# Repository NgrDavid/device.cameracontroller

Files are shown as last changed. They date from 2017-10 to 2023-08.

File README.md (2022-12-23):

## Harp Camera Trigger Control

This device allows to trigger up to 2 cameras at a predefined frequency pulse or 2 servo motors. Connect cameras to CAM0 TRIG and CAM1 TRIG ports.

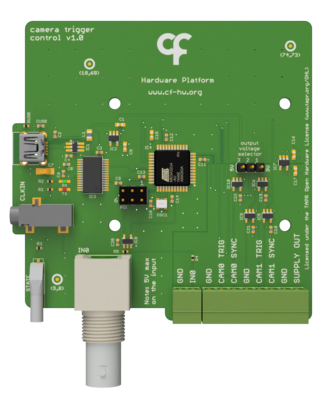
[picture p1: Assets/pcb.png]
harpcameratriggercontrol


### Key Features ###

* Separate sample frequency for each camera
* Alternate between camera triggering and servo motor control
* Each camera output can be handled as pure digital output

### Connectivity ###

* 1x clock sync input (CLKIN) [stereo jack]
* 1x USB (for computer) [USB type B]
* 1x 5V supply out [screw terminal]
* 4x digital outputs (I/O interface for 2 cameras): CAM0 TRIG, CAM0 SYNC, CAM1 TRIG, CAM1 SYNC [screw terminal]
* 1x digital input for general purpose or camera control (IN0) [BNC]

## Interface ##

The interface with the Harp board can be done through [Bonsai](https://bonsai-rx.org/) or a dedicated GUI (Graphical User Interface).

In order to use this GUI, there are some software that needs to be installed:

1 - Install the [drivers](https://bitbucket.org/fchampalimaud/downloads/downloads/UsbDriver-2.12.26.zip).

2 - Install the [runtime](https://bitbucket.org/fchampalimaud/downloads/downloads/Runtime-1.0.zip).

3 - Reboot the computer.

4 - Install the [GUI](https://bitbucket.org/fchampalimaud/downloads/downloads/Harp%20Camera%20Controller%20v1.0.1.zip).

## Licensing ##

Each subdirectory will contain a license or, possibly, a set of licenses if it involves both hardware and software.

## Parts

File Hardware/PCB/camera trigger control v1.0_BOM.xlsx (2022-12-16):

Part(s) | Quantity | Description | Distributor | Part. No.
IC1 | 1 | ESD Protection Low Cap | Mouser | 511-USBLC6-2SC6
IC2, IC7 | 2 | LDO 250mA Ultra-Lo Noise LDO Reg | Mouser | 595-LP5907MFX-3.3NPB
IC3 | 1 | IC USB USB to Serial UART Enhanced IC SSOP-28 | Mouser | 895-FT232RL
IC4 | 1 | ATXMEGA64A4U-AU, ATxmega, 32 MHz, 64 KB, 4 KB, 44, TQFP | Mouser | 556-ATXMEGA64A4U-AU
IC5, IC6, IC9, IC10 | 4 | Buffers e line drivers 1.65-5.5V Single Non-Inverting TTL | Mouser | 863-M74VHC1GT50DTT1G
IC8 | 1 | SingleBuffer / Driver, 1.65V to 5.5V, SOT-23-5 | Mouser | 595-SN74LVC1G125DBVR
C3, C4 | 2 | CAP CER 47pF 50V ±5% C0G 0402 | Mouser | 77-VJ0402A470JXACBC
CUSB | 1 | CAP CER 4.7nF 100V ±10% X7R 0402 | Mouser | 81-GRM155R72A472KA01
C2, C6, C8, C9, C10, C11, C12, C13, C18, C19, C20, C21, C22 | 13 | CAP CER 100nF 10V X5R 0402 | REEL | REEL
C14 | 1 | CAP CER 0.33uF 10V ±10% X5R 0402 | Mouser | GRM155R61A334KE15D
C7 | 1 | CAP TAN 4.7uF 6.3V ±10% 1206 | Mouser | 80-T491A475K006
C1, C5, C15, C16, C17 | 5 | CAP CER 10uF 10V ±10% X5R 0603 | Mouser | 81-GRM188R61A106KE9D
R1, R2 | 0 | DNI | DNI | DNI
R3 | 1 | RES SMD 68Ω OHM 5% 0402 | Mouser | 71-CRCW0402-68-E3
R4 | 1 | RES SMD 330Ω OHM 1% 0402 | Mouser | 667-ERJ-PA2F3300X
R5 | 1 | RES SMD 100kΩ 1% 0402 | REEL | REEL
RUSB | 1 | RES SMD 1MΩ 1% 0402 | Mouser | 652-CR0402FX-1004GLF
L1 | 1 | 40ohms 100MHz 1.5A Monolithic 0805 SMD | Mouser | 875-MI0805K400R-10
STATE | 1 | LED, Green, 1.6mm x 0.8mm, 566 nm, 2.1 V, 20 mA, 15 mcd | Mouser | 78-TLMP1100-GS08
RX, TX | 0 | DNI | DNI | DNI
OSC1 | 1 | 32MHz 10ppm | Mouser | 998-1001CI5032.0000T
PDI | 1 | 6P DR UNSHRD HRD | Mouser | 649-67996-206HLF
JP1 | 1 | 3POS Gold Male | Mouser | 649-68001-203HLF
 | 1 | SHUNT JUMPER, 2POS | Farnell | 2396301
USB | 1 | UX60-MB-5S8 | Mouser | 798-UX60-MB-5S8
USB Cable | 1 | USB A - MINI-B 0.8M - MINI-B 0.8M BLACK | Mouser | 538-88732-8502
IN0 | 1 | R.A. JACK 50 OHM | Mouser | 571-5227161-1
CLKIN | 1 | SMT 3.5 STEREO REEL | Mouser | 502-35RASMT2BHNTRX
 | 1 | Tubos de Luz LED CML LIGHTPIPE | Mouser | 606-7513D2-L
 | 1 | IMO 20.1550M/8-E Pluggable Terminal Block, 3.5 mm, 8 Ways | Farnell | 2575220
 | 1 | IMO 20.1550M/2-E Pluggable Terminal Block, 3.5 mm, 2 Ways | Farnell | 2575215
X1 | 1 | Horizontal, Header, 3.5 mm, 2 Ways, 10 A, 250 V, Through Hole Right Angle | Farnell | 20.155MH/2-E
X2 | 1 | Horizontal, Header, 3.5 mm, 8 Ways, 10 A, 250 V, Through Hole Right Angle | Farnell | 20.155MH/8-E
Components | 52
Licensed under the TAPR Open Hardware License (www.tapr.org/OHL)
Copyright 2017 Artur Silva and Filipe Carvalho

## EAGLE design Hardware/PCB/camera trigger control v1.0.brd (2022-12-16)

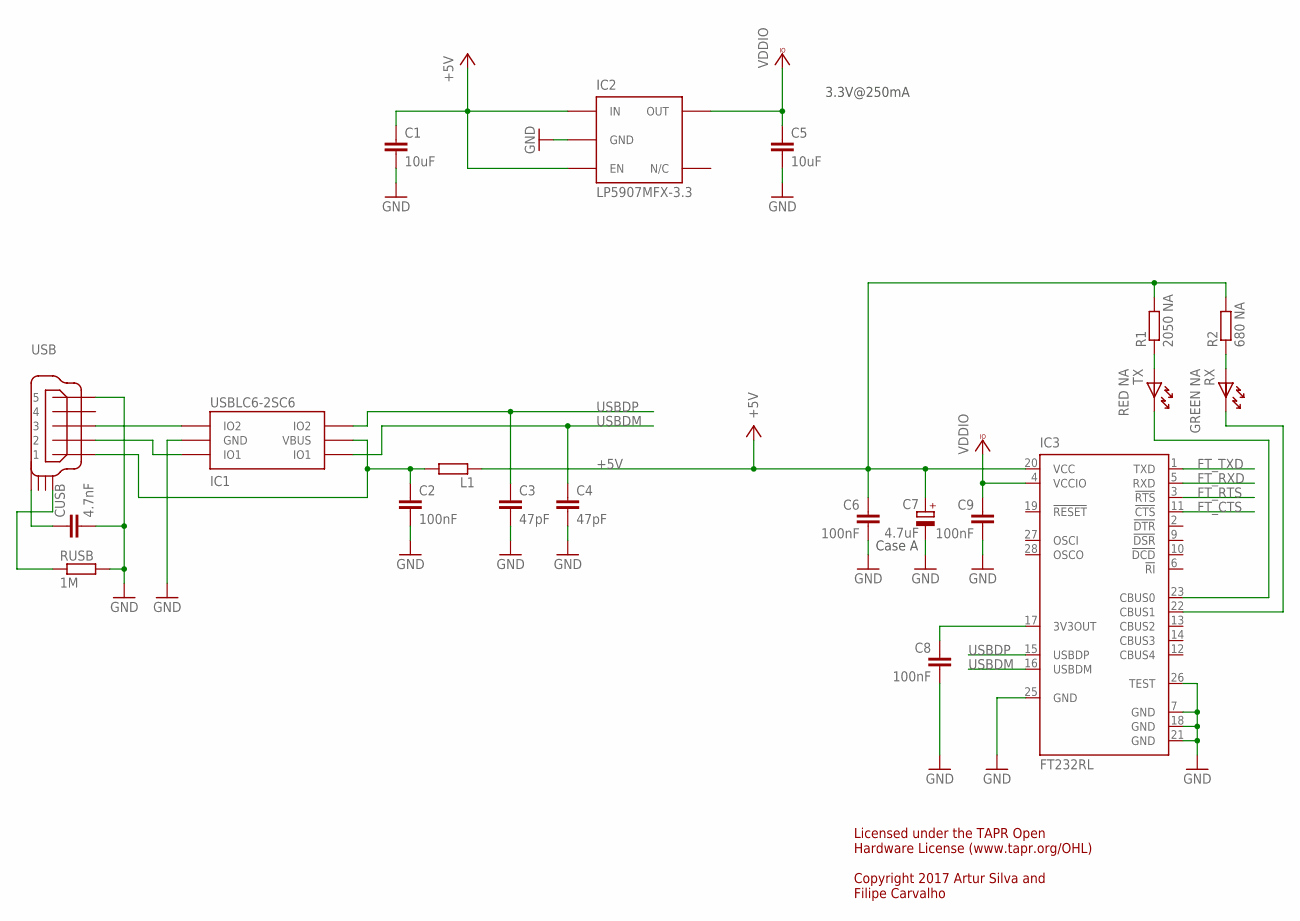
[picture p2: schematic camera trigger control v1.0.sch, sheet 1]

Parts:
C1, C5: 10uF; C0603
C2, C6, C8, C9: 100nF; C0402
C3, C4: 47pF; C0402
C7: 4.7uF; A/3216-18W
CUSB: 4.7nF; C0402
IC1: USBLC6-2SC6; SOT23-6L
IC2: LP5907MFX-3.3; TSOT23-5
IC3: FT232RL; SSOP28
L1: ???; R0805
R1: 2050 NA; R0402
R2: 680 NA; R0402
RUSB: 1M; R0402
RX: GREEN NA; LED_HAND
TX: RED NA; LED_HAND
USB: USB_MINI_B; 240-0002-1

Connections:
+5V: C1.1, C6.1, C7.+, IC2.1 (IN), IC2.3 (EN), IC3.20 (VCC), L1.1, R1.2, R2.2; also elsewhere on the board
FT_CTS: IC3.11 (!CTS); also elsewhere on the board
FT_RTS: IC3.3 (!RTS); also elsewhere on the board
FT_RXD: IC3.5 (RXD); also elsewhere on the board
FT_TXD: IC3.1 (TXD); also elsewhere on the board
GND: C1.2, C2.2, C3.2, C4.2, C5.2, C6.2, C7.-, C8.2, C9.2, CUSB.2, IC1.P$2 (GND), IC2.2 (GND), IC3.7 (GND), IC3.18 (GND), IC3.21 (GND), IC3.25 (GND), IC3.26 (TEST), RUSB.2, USB.P$5 (5); also elsewhere on the board
unnamed: C8.1, IC3.17 (3V3OUT)
unnamed: C2.1, IC1.P$5 (VBUS), L1.2, USB.P$1 (1)
unnamed: IC1.P$1 (IO1), USB.P$2 (2)
unnamed: R2.1, RX.A
unnamed: IC3.23 (CBUS0), TX.K
unnamed: IC3.22 (CBUS1), RX.K
unnamed: IC1.P$3 (IO2), USB.P$3 (3)
unnamed: CUSB.1, USB.SHIELD_4
unnamed: RUSB.1, USB.SHIELD_1
unnamed: R1.1, TX.A
USBDM: C4.1, IC1.P$6 (IO1), IC3.16 (USBDM)
USBDP: C3.1, IC1.P$4 (IO2), IC3.15 (USBDP)
VCCIO: C5.1, C9.1, IC2.5 (OUT), IC3.4 (VCCIO); also elsewhere on the board

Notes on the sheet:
Case A
3.3V@250mA
Licensed under the TAPR Open Hardware License (www.tapr.org/OHL) Copyright 2017 Artur Silva and Filipe Carvalho

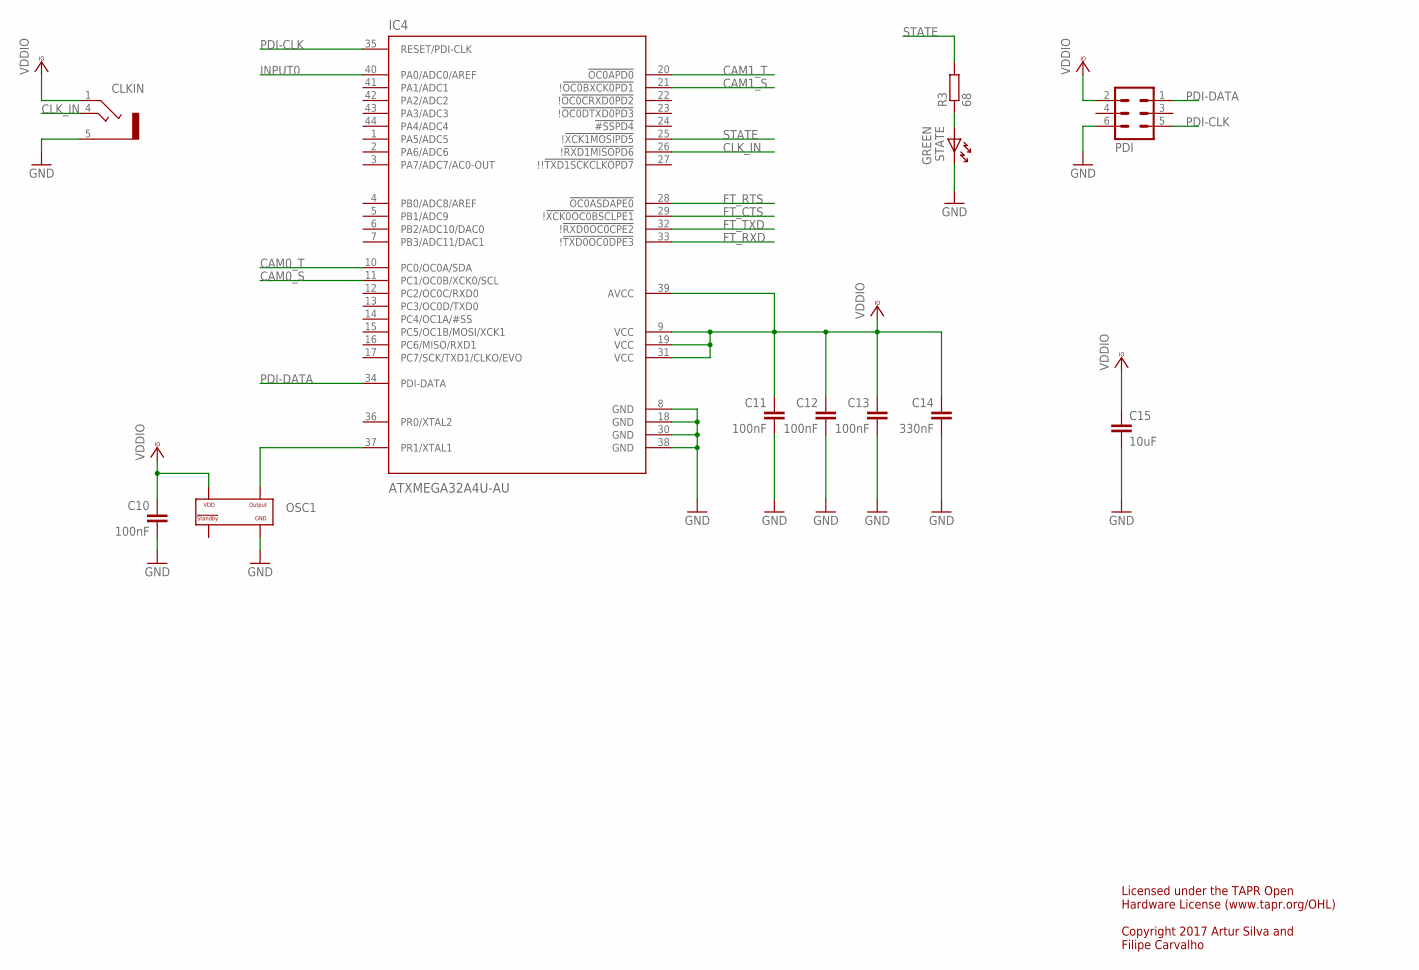
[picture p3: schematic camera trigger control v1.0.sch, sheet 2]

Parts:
C10, C11, C12, C13: 100nF; C0402
C14: 330nF; C0402
C15: 10uF; C0603
CLKIN: STEREO_JACK; 35RASMT2BHNTRX
IC4: ATXMEGA32A4U-AU; QFP80P1200X1200X120-44N
OSC1: OSCILLATOR; OSCILLATOR_3.2X2.5
PDI: MA03-2
R3: 68; R0402
STATE: GREEN; LED_HAND

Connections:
CAM0_S: IC4.11 (PC1/OC0B/XCK0/SCL); also elsewhere on the board
CAM0_T: IC4.10 (PC0/OC0A/SDA); also elsewhere on the board
CAM1_S: IC4.21 (!!OC0BXCK0PD1); also elsewhere on the board
CAM1_T: IC4.20 (!OC0APD0); also elsewhere on the board
CLK_IN: CLKIN.4, IC4.26 (!!RXD1MISOPD6)
FT_CTS: IC4.29 (!!XCK0OC0BSCLPE1); also elsewhere on the board
FT_RTS: IC4.28 (!OC0ASDAPE0); also elsewhere on the board
FT_RXD: IC4.33 (!!TXD0OC0DPE3); also elsewhere on the board
FT_TXD: IC4.32 (!!RXD0OC0CPE2); also elsewhere on the board
GND: C10.2, C11.2, C12.2, C13.2, C14.2, C15.2, CLKIN.5, IC4.8 (GND), IC4.18 (GND), IC4.30 (GND), IC4.38 (GND), OSC1.P$2 (GND), PDI.6, STATE.K; also elsewhere on the board
INPUT0: IC4.40 (PA0/ADC0/AREF); also elsewhere on the board
unnamed: R3.1, STATE.A
OSC1: IC4.37 (PR1/XTAL1), OSC1.P$3 (OUTPUT)
PDI-CLK: IC4.35 (RESET/PDI-CLK), PDI.5
PDI-DATA: IC4.34 (PDI-DATA), PDI.1
STATE: IC4.25 (!!XCK1MOSIPD5), R3.2
VCCIO: C10.1, C11.1, C12.1, C13.1, C14.1, C15.1, CLKIN.1, IC4.9 (VCC), IC4.19 (VCC), IC4.31 (VCC), IC4.39 (AVCC), OSC1.P$4 (VDD), PDI.2; also elsewhere on the board

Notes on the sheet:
Licensed under the TAPR Open Hardware License (www.tapr.org/OHL) Copyright 2017 Artur Silva and Filipe Carvalho

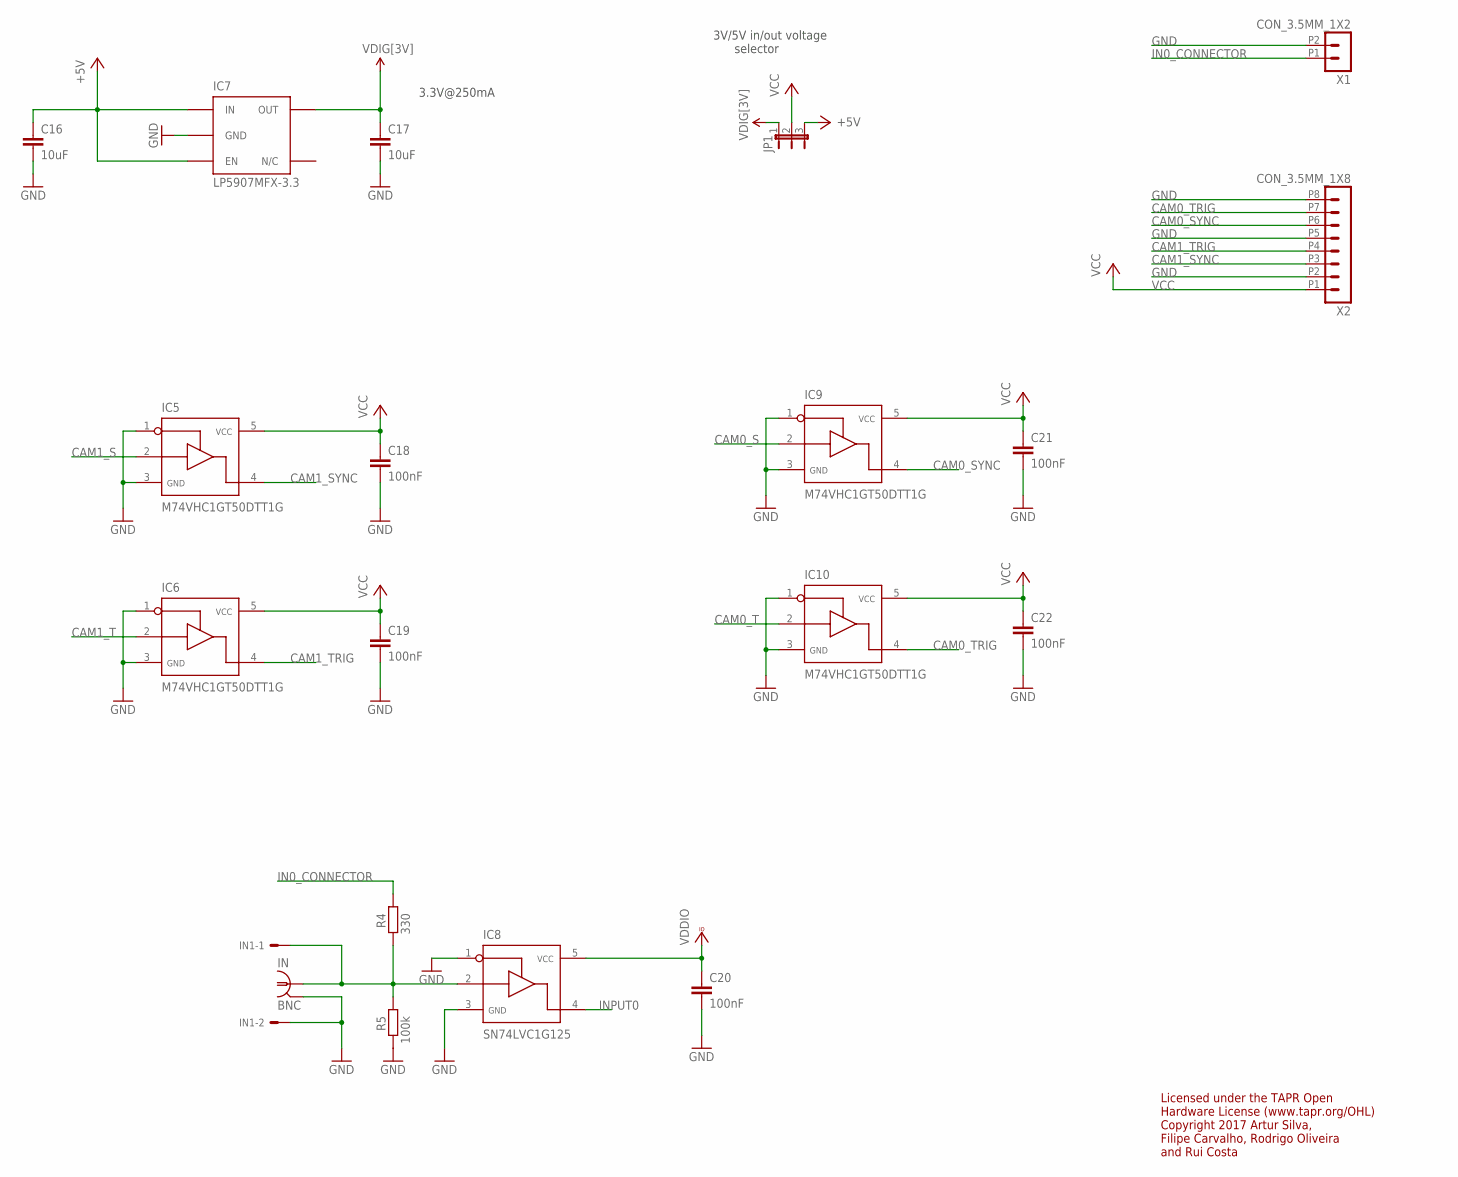
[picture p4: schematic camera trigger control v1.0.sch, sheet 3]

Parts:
C16, C17: 10uF; C0603
C18, C19, C20, C21, C22: 100nF; C0402
IC5, IC6, IC9, IC10: M74VHC1GT50DTT1G; SOT23-5
IC7: LP5907MFX-3.3; TSOT23-5
IC8: SN74LVC1G125; SOT23-5
IN: BNC; BNC_RA
IN1: 22-05-7028-02; 7395-02
JP1: JP2E; JP2
R4: 330; R0402
R5: 100k; R0402
X1: CON_3.5MM_1X2
X2: CON_3.5MM_1X8

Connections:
+5V: C16.1, IC7.1 (IN), IC7.3 (EN), JP1.3; also elsewhere on the board
CAM0_S: IC9.2; also elsewhere on the board
CAM0_SYNC: IC9.4, X2.P6 (6)
CAM0_T: IC10.2; also elsewhere on the board
CAM0_TRIG: IC10.4, X2.P7 (7)
CAM1_S: IC5.2; also elsewhere on the board
CAM1_SYNC: IC5.4, X2.P3 (3)
CAM1_T: IC6.2; also elsewhere on the board
CAM1_TRIG: IC6.4, X2.P4 (4)
GND: C16.2, C17.2, C18.2, C19.2, C20.2, C21.2, C22.2, IC5.1, IC5.3, IC6.1, IC6.3, IC7.2 (GND), IC8.1, IC8.3, IC9.1, IC9.3, IC10.1, IC10.3, IN.2, IN1.2, R5.2, X1.P2 (2), X2.P2 (2), X2.P5 (5), X2.P8 (8); also elsewhere on the board
IN0: IC8.2, IN.1, IN1.1, R4.2, R5.1
IN0_CONNECTOR: R4.1, X1.P1 (1)
INPUT0: IC8.4; also elsewhere on the board
VCC: C18.1, C19.1, C21.1, C22.1, IC5.5, IC6.5, IC9.5, IC10.5, JP1.2, X2.P1 (1)
VCCIO: C20.1, IC8.5; also elsewhere on the board
VDIG[3V]: C17.1, IC7.5 (OUT), JP1.1

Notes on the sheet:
3.3V@250mA
3V/5V in/out voltage selector
Licensed under the TAPR Open Hardware License (www.tapr.org/OHL) Copyright 2017 Artur Silva, Filipe Carvalho, Rodrigo Oliveira and Rui Costa

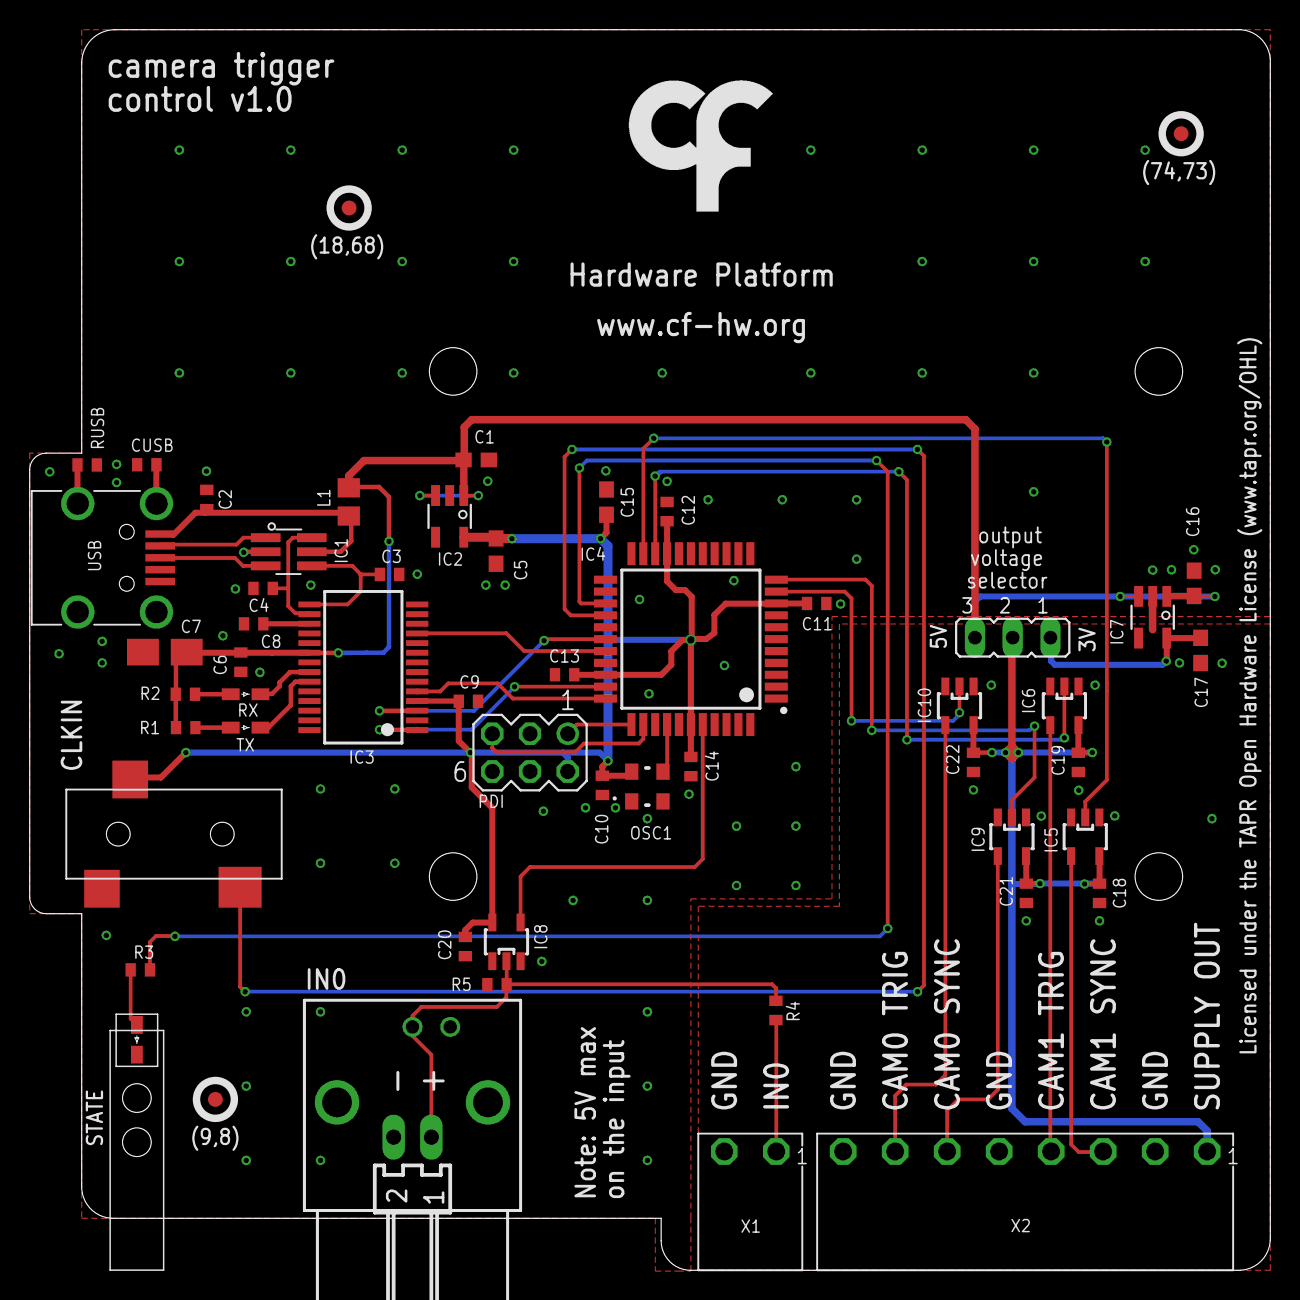
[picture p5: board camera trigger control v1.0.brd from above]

Board: 2 copper layers, 83.5 x 83.5 mm, 57 parts (0 on the bottom side), 38 nets.

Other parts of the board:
U$1: LED_PIPE_7513D2-L
U$4, U$5, U$6: FIDUCIAL
U$9: LOGO_6

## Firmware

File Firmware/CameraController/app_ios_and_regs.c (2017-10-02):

#include <avr/io.h>
#include "hwbp_core_types.h"
#include "app_ios_and_regs.h"

/************************************************************************/
/* Configure and initialize IOs                                         */
/************************************************************************/
void init_ios(void)
{	/* Configure input pins */
	io_pin2in(&PORTA, 0, PULL_IO_TRISTATE, SENSE_IO_EDGES_BOTH);         // INPUT0

	/* Configure input interrupts */
	io_set_int(&PORTA, INT_LEVEL_LOW, 0, (1<<0), false);                 // INPUT0

	/* Configure output pins */
	io_pin2out(&PORTC, 0, OUT_IO_DIGITAL, IN_EN_IO_EN);                  // CAM0_TRIG
	io_pin2out(&PORTC, 1, OUT_IO_DIGITAL, IN_EN_IO_EN);                  // CAM0_SYNC
	io_pin2out(&PORTD, 0, OUT_IO_DIGITAL, IN_EN_IO_EN);                  // CAM1_TRIG
	io_pin2out(&PORTD, 1, OUT_IO_DIGITAL, IN_EN_IO_EN);                  // CAM1_SYNC

	/* Initialize output pins */
	clr_CAM0_TRIG;
	clr_CAM0_SYNC;
	clr_CAM1_TRIG;
	clr_CAM1_SYNC;
}

/************************************************************************/
/* Registers' stuff                                                     */
/************************************************************************/
AppRegs app_regs;

uint8_t app_regs_type[] = {
	TYPE_U8,
	TYPE_U8,
	TYPE_U8,
	TYPE_U8,
	TYPE_U8,
	TYPE_U8,
	TYPE_U8,
	TYPE_U8,
	TYPE_U8,
	TYPE_U8,
	TYPE_U8,
	TYPE_U8,
	TYPE_U8,
	TYPE_U8,
	TYPE_U8,
	TYPE_U8,
	TYPE_U8,
	TYPE_U8,
	TYPE_U16,
	TYPE_U16,
	TYPE_U16,
	TYPE_U8,
	TYPE_U16,
	TYPE_U16,
	TYPE_U16,
	TYPE_U8,
	TYPE_U8,
	TYPE_U8
};

uint16_t app_regs_n_elements[] = {
	1,
	1,
	1,
	1,
	1,
	1,
	1,
	1,
	1,
	1,
	1,
	1,
	1,
	1,
	1,
	1,
	1,
	1,
	1,
	1,
	1,
	1,
	1,
	1,
	1,
	1,
	1,
	1
};

uint8_t *app_regs_pointer[] = {
	(uint8_t*)(&app_regs.REG_START_CAMS),
	(uint8_t*)(&app_regs.REG_STOP_CAMS),
	(uint8_t*)(&app_regs.REG_ENABLE_MOTORS),
	(uint8_t*)(&app_regs.REG_DISABLE_MOTORS),
	(uint8_t*)(&app_regs.REG_SET_OUTPUTS),
	(uint8_t*)(&app_regs.REG_CLR_OUTPUTS),
	(uint8_t*)(&app_regs.REG_OUTPUTS),
	(uint8_t*)(&app_regs.REG_INPUT0),
	(uint8_t*)(&app_regs.REG_CAM0),
	(uint8_t*)(&app_regs.REG_CAM1),
	(uint8_t*)(&app_regs.REG_SYNC0),
	(uint8_t*)(&app_regs.REG_SYNC1),
	(uint8_t*)(&app_regs.REG_MOTORS_STATE),
	(uint8_t*)(&app_regs.REG_RESERVED0),
	(uint8_t*)(&app_regs.REG_SYNC_INTERVAL),
	(uint8_t*)(&app_regs.REG_RESERVED1),
	(uint8_t*)(&app_regs.REG_IN0_MODE),
	(uint8_t*)(&app_regs.REG_CAM0_MODE),
	(uint8_t*)(&app_regs.REG_CAM0_FREQ),
	(uint8_t*)(&app_regs.REG_CAM0_MMODE_PERIOD),
	(uint8_t*)(&app_regs.REG_CAM0_MMODE_PULSE),
	(uint8_t*)(&app_regs.REG_CAM1_MODE),
	(uint8_t*)(&app_regs.REG_CAM1_FREQ),
	(uint8_t*)(&app_regs.REG_CAM1_MMODE_PERIOD),
	(uint8_t*)(&app_regs.REG_CAM1_MMODE_PULSE),
	(uint8_t*)(&app_regs.REG_RESERVED2),
	(uint8_t*)(&app_regs.REG_RESERVED3),
	(uint8_t*)(&app_regs.REG_EVT_EN)
};

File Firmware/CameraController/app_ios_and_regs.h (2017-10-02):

#ifndef _APP_IOS_AND_REGS_H_
#define _APP_IOS_AND_REGS_H_
#include "cpu.h"

void init_ios(void);
/************************************************************************/
/* Definition of input pins                                             */
/************************************************************************/
// INPUT0                 Description: Input 0

#define read_INPUT0 read_io(PORTA, 0)           // INPUT0

/************************************************************************/
/* Definition of output pins                                            */
/************************************************************************/
// CAM0_TRIG              Description: Camera 0 trigger
// CAM0_SYNC              Description: Camera 0 synchronizer
// CAM1_TRIG              Description: Camera 1 trigger
// CAM1_SYNC              Description: Camera 1 synchronizer

/* CAM0_TRIG */
#define set_CAM0_TRIG set_io(PORTC, 0)
#define clr_CAM0_TRIG clear_io(PORTC, 0)
#define tgl_CAM0_TRIG toggle_io(PORTC, 0)
#define read_CAM0_TRIG read_io(PORTC, 0)

/* CAM0_SYNC */
#define set_CAM0_SYNC set_io(PORTC, 1)
#define clr_CAM0_SYNC clear_io(PORTC, 1)
#define tgl_CAM0_SYNC toggle_io(PORTC, 1)
#define read_CAM0_SYNC read_io(PORTC, 1)

/* CAM1_TRIG */
#define set_CAM1_TRIG set_io(PORTD, 0)
#define clr_CAM1_TRIG clear_io(PORTD, 0)
#define tgl_CAM1_TRIG toggle_io(PORTD, 0)
#define read_CAM1_TRIG read_io(PORTD, 0)

/* CAM1_SYNC */
#define set_CAM1_SYNC set_io(PORTD, 1)
#define clr_CAM1_SYNC clear_io(PORTD, 1)
#define tgl_CAM1_SYNC toggle_io(PORTD, 1)
#define read_CAM1_SYNC read_io(PORTD, 1)


/************************************************************************/
/* Registers' structure                                                 */
/************************************************************************/
typedef struct
{
	uint8_t REG_START_CAMS;
	uint8_t REG_STOP_CAMS;
	uint8_t REG_ENABLE_MOTORS;
	uint8_t REG_DISABLE_MOTORS;
	uint8_t REG_SET_OUTPUTS;
	uint8_t REG_CLR_OUTPUTS;
	uint8_t REG_OUTPUTS;
	uint8_t REG_INPUT0;
	uint8_t REG_CAM0;
	uint8_t REG_CAM1;
	uint8_t REG_SYNC0;
	uint8_t REG_SYNC1;
	uint8_t REG_MOTORS_STATE;
	uint8_t REG_RESERVED0;
	uint8_t REG_SYNC_INTERVAL;
	uint8_t REG_RESERVED1;
	uint8_t REG_IN0_MODE;
	uint8_t REG_CAM0_MODE;
	uint16_t REG_CAM0_FREQ;
	uint16_t REG_CAM0_MMODE_PERIOD;
	uint16_t REG_CAM0_MMODE_PULSE;
	uint8_t REG_CAM1_MODE;
	uint16_t REG_CAM1_FREQ;
	uint16_t REG_CAM1_MMODE_PERIOD;
	uint16_t REG_CAM1_MMODE_PULSE;
	uint8_t REG_RESERVED2;
	uint8_t REG_RESERVED3;
	uint8_t REG_EVT_EN;
} AppRegs;

/************************************************************************/
/* Registers' address                                                   */
/************************************************************************/
/* Registers */
#define ADD_REG_START_CAMS                  32 // U8     Start cameras triggering
#define ADD_REG_STOP_CAMS                   33 // U8     Stop cameras triggering
#define ADD_REG_ENABLE_MOTORS               34 // U8     Start sending pulses to the motors
#define ADD_REG_DISABLE_MOTORS              35 // U8     Stop sending ulses to the motors
#define ADD_REG_SET_OUTPUTS                 36 // U8     Set the outputs
#define ADD_REG_CLR_OUTPUTS                 37 // U8     Set the outputs
#define ADD_REG_OUTPUTS                     38 // U8     Control outputs' state
#define ADD_REG_INPUT0                      39 // U8     Input0's state (read only)
#define ADD_REG_CAM0                        40 // U8     Camera 0's triggering (read only)
#define ADD_REG_CAM1                        41 // U8     Camera 1's triggering (read only)
#define ADD_REG_SYNC0                       42 // U8     Sync 0 was set (read only)
#define ADD_REG_SYNC1                       43 // U8     Sync 1 was set (read only)
#define ADD_REG_MOTORS_STATE                44 // U8     State of the motors (enabled or disabled) (read only)
#define ADD_REG_RESERVED0                   45 // U8     Reserved
#define ADD_REG_SYNC_INTERVAL               46 // U8     Configures the interval in seconds between each sync pulse
#define ADD_REG_RESERVED1                   47 // U8     Reserved
#define ADD_REG_IN0_MODE                    48 // U8     Select the functionality of Input 0
#define ADD_REG_CAM0_MODE                   49 // U8     Configures when the camera is triggered
#define ADD_REG_CAM0_FREQ                   50 // U16    Configures the camera 0's sample frequency [1;600]
#define ADD_REG_CAM0_MMODE_PERIOD           51 // U16    Configures the servo motor period (us) when using motor controller mode (sensitive to 2 us)
#define ADD_REG_CAM0_MMODE_PULSE            52 // U16    Configures the servo motor pulse (us) when using motor controller mode (sensitive to 2 us)
#define ADD_REG_CAM1_MODE                   53 // U8     Configures when the camera is triggered
#define ADD_REG_CAM1_FREQ                   54 // U16    Configures the camera 1's sample frequency [1;600]
#define ADD_REG_CAM1_MMODE_PERIOD           55 // U16    Configures the servo motor period (us) when using motor controller mode (sensitive to 2 us)
#define ADD_REG_CAM1_MMODE_PULSE            56 // U16    Configures the servo motor pulse (us) when using motor controller mode (sensitive to 2 us)
#define ADD_REG_RESERVED2                   57 // U8     Reserved for possible future use
#define ADD_REG_RESERVED3                   58 // U8     Reserved for possible future use
#define ADD_REG_EVT_EN                      59 // U8     Enable the Events

/************************************************************************/
/* PWM Generator registers' memory limits                               */
/*                                                                      */
/* DON'T change the APP_REGS_ADD_MIN value !!!                          */
/* DON'T change these names !!!                                         */
/************************************************************************/
/* Memory limits */
#define APP_REGS_ADD_MIN                    0x20
#define APP_REGS_ADD_MAX                    0x3B
#define APP_NBYTES_OF_REG_BANK              34

/************************************************************************/
/* Registers' bits                                                      */
/************************************************************************/
#define B_START_CAM0                       (1<<0)       // Start camera 0
#define B_START_CAM1                       (1<<1)       // Start camera 1
#define B_STOP_CAM0                        (1<<0)       // Stop camera 0
#define B_STOP_CAM1                        (1<<1)       // Stop camera 1
#define B_EN_MOTOR0                        (1<<0)       // Enable motor 0
#define B_EN_MOTOR1                        (1<<1)       // Enable motor 1
#define B_DIS_MOTOR0                       (1<<0)       // Disable motor 0
#define B_DIS_MOTOR1                       (1<<1)       // Disable motor 1
#define B_OUT_CAM_TRIG0                    (1<<0)       // Trigger 0
#define B_OUT_CAM_SYNC0                    (1<<1)       // Sync 0
#define B_OUT_CAM_TRIG1                    (1<<2)       // Trigger 1
#define B_OUT_CAM_SYNC1                    (1<<3)       // Sync 1
#define B_IN0                              (1<<0)       // Input 0
#define B_CAM0                             (1<<0)       // Camera 0 was triggered
#define B_CAM1                             (1<<0)       // Camera 1 was triggered
#define B_SYNC0                            (1<<0)       // Camera 0's sync changed the state
#define B_SYNC1                            (1<<0)       // Camera 1's sync changed the state
#define B_MOTOR0                           (1<<0)       // State of motor 0 (enabled = 1)
#define B_MOTOR1                           (1<<1)       // State of motor 1 (enabled = 1)
#define MSK_IN0_MODE                       (7<<0)       // 
#define GM_IN0_H_CAM0                      (0<<0)       // When logic 1: enable camera 0 or motor 0
#define GM_IN0_H_CAM1                      (1<<0)       // When logic 1: enable camera 1 or motor 1
#define GM_IN0_H_BOTH                      (2<<0)       // When logic 1: enable both cameras or motors
#define GM_IN0_L_CAM0                      (3<<0)       // When logic 0: enable camera 0 or motor 0
#define GM_IN0_L_CAM1                      (4<<0)       // When logic 0: enable camera 1 or motor 1
#define GM_IN0_L_BOTH                      (5<<0)       // When logic 0: enable both cameras or motors
#define GM_IN0_NOT_USED                    (6<<0)       // Used as a digital input only
#define MSK_CAM0_MODE                      (1<<0)       // Options for CAM0
#define GM_CAM0_MODE_CAM                   (0<<0)       // The camera 0 is triggered at a configured frequency
#define GM_CAM0_MODE_MOTOR                 (1<<0)       // Used in servo motor controller mode
#define MSK_CAM1_MODE                      (1<<0)       // Options for CAM1
#define GM_CAM1_MODE_CAM                   (0<<0)       // The camera 1 is triggered at a configured frequency
#define GM_CAM1_MODE_MOTOR                 (1<<0)       // Used in servo motor controller mode
#define B_EVT_CAMS                         (1<<0)       // Events of registers CAMs and SYNCs
#define B_EVT_IN0                          (1<<1)       // Event of register INPUT0

#endif /* _APP_REGS_H_ */

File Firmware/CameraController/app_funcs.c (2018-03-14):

#include "app_funcs.h"
#include "app_ios_and_regs.h"
#include "hwbp_core.h"

#define F_CPU 32000000
#include <util/delay.h>


/************************************************************************/
/* Create pointers to functions                                         */
/************************************************************************/
extern AppRegs app_regs;

void (*app_func_rd_pointer[])(void) = {
	&app_read_REG_START_CAMS,
	&app_read_REG_STOP_CAMS,
	&app_read_REG_ENABLE_MOTORS,
	&app_read_REG_DISABLE_MOTORS,
	&app_read_REG_SET_OUTPUTS,
	&app_read_REG_CLR_OUTPUTS,
	&app_read_REG_OUTPUTS,
	&app_read_REG_INPUT0,
	&app_read_REG_CAM0,
	&app_read_REG_CAM1,
	&app_read_REG_SYNC0,
	&app_read_REG_SYNC1,
	&app_read_REG_MOTORS_STATE,
	&app_read_REG_RESERVED0,
	&app_read_REG_SYNC_INTERVAL,
	&app_read_REG_RESERVED1,
	&app_read_REG_IN0_MODE,
	&app_read_REG_CAM0_MODE,
	&app_read_REG_CAM0_FREQ,
	&app_read_REG_CAM0_MMODE_PERIOD,
	&app_read_REG_CAM0_MMODE_PULSE,
	&app_read_REG_CAM1_MODE,
	&app_read_REG_CAM1_FREQ,
	&app_read_REG_CAM1_MMODE_PERIOD,
	&app_read_REG_CAM1_MMODE_PULSE,
	&app_read_REG_RESERVED2,
	&app_read_REG_RESERVED3,
	&app_read_REG_EVT_EN
};

bool (*app_func_wr_pointer[])(void*) = {
	&app_write_REG_START_CAMS,
	&app_write_REG_STOP_CAMS,
	&app_write_REG_ENABLE_MOTORS,
	&app_write_REG_DISABLE_MOTORS,
	&app_write_REG_SET_OUTPUTS,
	&app_write_REG_CLR_OUTPUTS,
	&app_write_REG_OUTPUTS,
	&app_write_REG_INPUT0,
	&app_write_REG_CAM0,
	&app_write_REG_CAM1,
	&app_write_REG_SYNC0,
	&app_write_REG_SYNC1,
	&app_write_REG_MOTORS_STATE,
	&app_write_REG_RESERVED0,
	&app_write_REG_SYNC_INTERVAL,
	&app_write_REG_RESERVED1,
	&app_write_REG_IN0_MODE,
	&app_write_REG_CAM0_MODE,
	&app_write_REG_CAM0_FREQ,
	&app_write_REG_CAM0_MMODE_PERIOD,
	&app_write_REG_CAM0_MMODE_PULSE,
	&app_write_REG_CAM1_MODE,
	&app_write_REG_CAM1_FREQ,
	&app_write_REG_CAM1_MMODE_PERIOD,
	&app_write_REG_CAM1_MMODE_PULSE,
	&app_write_REG_RESERVED2,
	&app_write_REG_RESERVED3,
	&app_write_REG_EVT_EN
};

extern void start_camera0(void);
extern void start_camera1(void);
extern void stop_camera0(void);
extern void stop_camera1(void);
extern void enable_motor0(void);
extern void enable_motor1(void);
extern void disable_motor0(void);
extern void disable_motor1(void);
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

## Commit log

2017-09-29 Added first files.
    [registers.xls]
2017-10-02 Update registers.xls to final list.
    [registers.xls]
2017-10-02 Update Events Enable register to U8.
    [registers.xls]
2017-10-02 Corrected several bugs and small updates on the registers.xls file.
    [registers.xls]
2017-10-02 Updated bitmask of register OUTPUTS.
    [registers.xls]
2017-10-02 Added a new feature that stops the current behavior when goes into Standby Mode.
2017-10-06 Added ability to start camera imeddiatly after receive the IN0 trigger.
2017-10-12 Added a new feature that allows the motor to start immediatly depending on the IN0 state and IN0 configuration.
2018-01-15 Updated to Harp version 1.1.
    [registers.xls]
2018-03-04 Increased lower limit of the camera frequency to 2 Hz (1 Hz was not working properly).
2018-03-14 Corrected issue: when stopping the camera triggering, the last pulse was not correct.
2018-03-14 Updated to Harp version 1.4.
    [registers.xls]
2022-12-16 Add PCB and BOM files
    [camera trigger control v1.0.brd, camera trigger control v1.0.sch, camera trigger control v1.0_BOM.xlsx]
2022-12-23 refactor repository structure
    [camera trigger control v1.0.brd, camera trigger control v1.0.sch, camera trigger control v1.0_BOM.xlsx]
2023-08-20 Update PCB image asset
2023-08-22 Change start core parameters
    [registers.xls]
2024-11-13 Update device schema source
